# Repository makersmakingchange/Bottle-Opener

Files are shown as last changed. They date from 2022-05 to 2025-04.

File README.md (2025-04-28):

# Bottle Opener
The Bottle Opener is a simple, low-cost, 3D-printable handheld tool to help those with arthritis, limited finger dexterity or other related disabilities open or close plastic screw-on caps on various beverage bottles, cleaning products, condiments. The bottle opener allows users to remove or replace the lids of these jugs with a small squeeze on a large, rounded gripping surface. The Bottle Opener has several modified versions to open different sizes of containers. The different sizes are named by the approximate diameter of the caps they can open in millimeters.

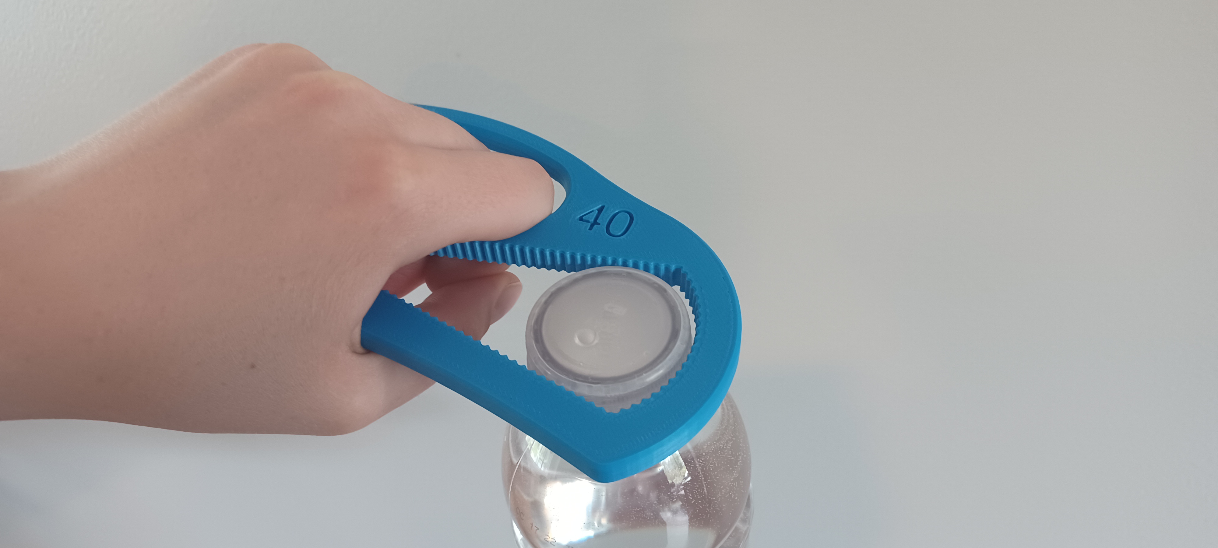
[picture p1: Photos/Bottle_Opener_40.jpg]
Bottle_Opener


## More info at
- [Makers Making Change Project Page](https://makersmakingchange.com/project/bottle-opener/)

## Getting Started

### 1. Print the 3D Printable components

Print the components according to the instructions in the [3D Print Guide](/Documentation/Bottle_Opener_3D_Print_Guide_V1.0.pdf).

All of the files and individual print files can be in the [/Build_Files](/Build_Files) folder.

### 2. Sizing

There are 5 different sizes of bottle opener to suit the different sizes of plastic caps on various bottles and containers. The [Summary](/Documentation/Bottle_Opener_Summary_V1.0.pdf) contains information on examples of different bottles that can be opened with the different sizes of bottle openers. A [Printable Sizing Sheet](/Documentation/Bottle_Opener_Printable_Sizing_Chart.pdf) has been provided to match bottle caps to the suitable bottle opener. Make sure to check "actual size" in the print settings so the image remains to-scale.

### 3. Bill of Materials

The [Bill of Materials](/Documentation/Bottle_Opener_BOM_V1.0.csv) lists the cost of building the different sizes of Bottle Openers.

## Files
### Documentation
| Document              | Version | Link |
|-----------------------|---------|------|
| Summary               | 1.0     | [Bottle_Opener_Summary](/Documentation/Bottle_Opener_Summary_V1.0.pdf)     |
| 3D Print Guide        | 1.0     | [Bottle_Opener_3D_Print_Guide](/Documentation/Bottle_Opener_3D_Print_Guide_V1.0.pdf)     |
| Design Rationale      | 1.0     | [Bottle_Opener_Design_Rationale](/Documentation/Bottle_Opener_Design_Rationale_V1.0.pdf)     |
| Bill of Materials     | 1.0     | [Bottle_Opener_Bill_of_Materials](/Documentation/Bottle_Opener_BOM_V1.0.csv)     |
| Maker Checklist       | 1.0     | [Bottle_Opener_Maker_Checklist](/Documentation/Bottle_Opener_Maker_Checklist_V1.0.pdf)     |
| User Guide            | 1.0     | [Bottle_Opener_User_Guide](/Documentation/Bottle_Opener_User_Guide_V1.0.pdf)    |
| Changelog             | 1.0     | [Bottle_Opener_Changelog](/Documentation/Bottle_Opener_Changelog_V1.0.pdf)     |
| Printable Sizing Chart| 1.0     | [Bottle_Opener_Printable_Sizing_Chart](/Documentation/Bottle_Opener_Printable_Sizing_Chart.pdf)     |

### Design Files
 - [CAD Files](/Design_Files/CAD_Files/)
   - [STEP Files](/Design_Files/CAD_Files/Step_Files/)
   - [Autodesk Fusion Files](/Design_Files/CAD_Files/Autodesk_Fusion/)
   - [Profile Sketch](/Design_Files/CAD_Files/Bottle_Opener_40_Sketch.png)

### Build Files
 - [3D Printing Files](/Build_Files)

## Attribution
The source of the original design is unknown. Various improvement and documentation have been completed by the Neil Squire Society / Makers Making Change.

### Contributors
 - Amanda Tuey. Neil Squire / Makers Making Change.
 - Kristina Mok. Neil Squire / Makers Making Change.
 - Taz Oldaker. Neil Squire / Makers Making Change.
 - Jake McIvor. Neil Squire / Makers Making Change.

## License
<br /><span xmlns:dct="http://purl.org/dc/terms/" property="dct:title">Bottle Opener</span> by <a xmlns:cc="http://creativecommons.org/ns#" href="www.makersmakingchange.com" property="cc:attributionName" rel="cc:attributionURL">Neil Squire</a> is licensed under a <a rel="license" href="http://creativecommons.org/licenses/by-sa/4.0/">Creative Commons Attribution-ShareAlike 4.0 International License</a>.

---
<!-- ABOUT MMC START -->
## About Makers Making Change
[Makers Making Change Logo](https://www.makersmakingchange.com/)

Makers Making Change is a program of [Neil Squire](https://www.neilsquire.ca/), a Canadian non-profit that uses technology, knowledge, and passion to empower people with disabilities.

Makers Making Change leverages the capacity of community based Makers, Disability Professionals and Volunteers to develop and deliver affordable Open Source Assistive Technologies.

 - Website: [www.MakersMakingChange.com](https://www.makersmakingchange.com/)
 - GitHub: [makersmakingchange](https://github.com/makersmakingchange)
 - Bluesky: [@makersmakingchange.bsky.social](https://bsky.app/profile/makersmakingchange.bsky.social)
 - Instagram: [@makersmakingchange](https://www.instagram.com/makersmakingchange)
 - Facebook: [makersmakechange](https://www.facebook.com/makersmakechange)
 - LinkedIn: [Neil Squire Society](https://www.linkedin.com/company/neil-squire-society/)
 - Thingiverse: [makersmakingchange](https://www.thingiverse.com/makersmakingchange/about)
 - Printables: [MakersMakingChange](https://www.printables.com/@MakersMakingChange)

### Contact Us
For technical questions, to get involved, or to share your experience we encourage you to [visit our website](https://www.makersmakingchange.com/) or [contact us](https://www.makersmakingchange.com/s/contact).
<!-- ABOUT MMC END -->

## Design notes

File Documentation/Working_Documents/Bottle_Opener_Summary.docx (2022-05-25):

# Title

Bottle Opener

## Subtitle

A tool to open screw on caps up to 50 mm in diameter.

## Device Specifications

Stage: Recently Added

Designer: Makers Making Change

Material Cost: $0 - $10

Disability Type: Mobility / Physical

Capabilities Needed: 3D Printing

Usage:

- Aids for Daily Living (ADL)
- Mobility

Difficulty: Beginner

Time to Complete: 1-4hr

License: Attribution - Non-Commercial - ShareAlike 4.0 International

## Device Details

### Overview

The Bottle Opener is a simple, low-cost, 3D-printable handheld tool to help those with arthritis, limited finger dexterity or other related disabilities open or close plastic screw-on caps on various beverage bottles, cleaning products, condiments. The bottle opener allows users to remove or replace the lids of these jugs with a small squeeze on a large, rounded gripping surface. The Bottle Opener has several modified versions to open different sizes of containers. The different sizes are named by the approximate diameter of the caps they can open in millimeters.

### Usage

Slide the toothed gripping surface on top of the lid of the container, then while squeezing the handle to grip the lid, twist either the container or the device to remove or screw on the lid.

### Cost

The cost of this device includes only the filament used to 3D print the device/devices. Each device requires slightly over $1 CAD worth of PLA filament.

### Build Instructions

This device consists of a single 3d printed part. The necessary files and 3D printing instructions are provided in the linked GitHub repository.

#### Skills Required

- 3D Printing

#### Time Required

- 3D Printing: ~3.5 hours

#### 3D Printing

Refer to the Large Bottle Opener 3D Printing Guide.

Sizing

There are five different sizes of Bottle Openers to suit different size caps on bottles and containers.

Bottle Opener Version | Compatible Diameter of Caps | Examples of compatible Bottles and Containers (May vary between brands) | Image Example of compatible Bottles

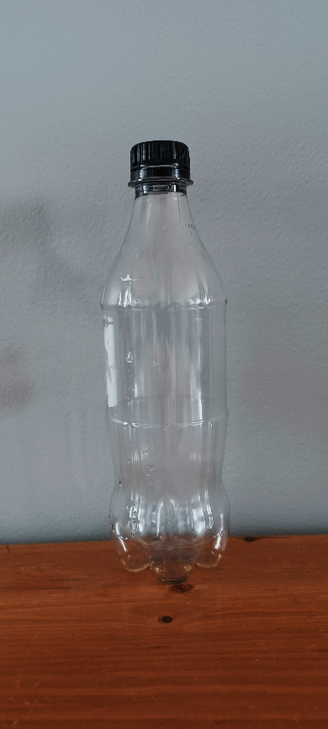
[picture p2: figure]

Bottle Opener 30 | 28 – 30 mm | - Pop bottles of all sizes (355 mL to 2 L) - Bottled Water of all sizes (355 mL to 2 L) - Milk Carton 2 L - Juice Carton 2 L

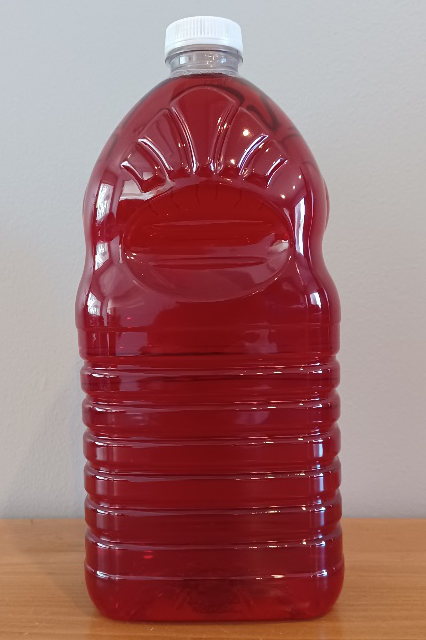
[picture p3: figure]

Bottle Opener 35 | 33 – 36 mm | - Juice Jug (Some brands) 1.89 L - Ketchup Bottle 1 L - Juice Carton 900 mL

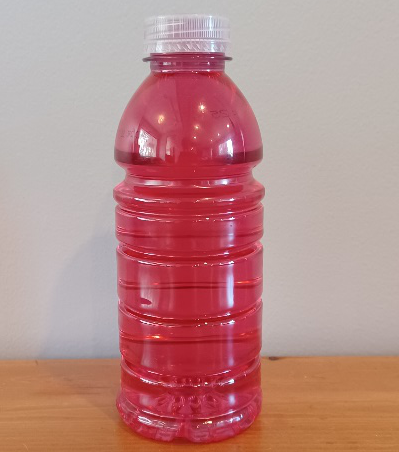
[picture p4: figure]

Bottle Opener 40 | 38 – 41 mm | - Sports Drink 591 mL - Sports Drink 950 mL - Juice Bottle 473 mL - Iced Tea Bottle 473 mL - Milk Bottle 473 mL - Milk Jug 2 L - Milk Jug 4 L - Kefir Bottle 1 L

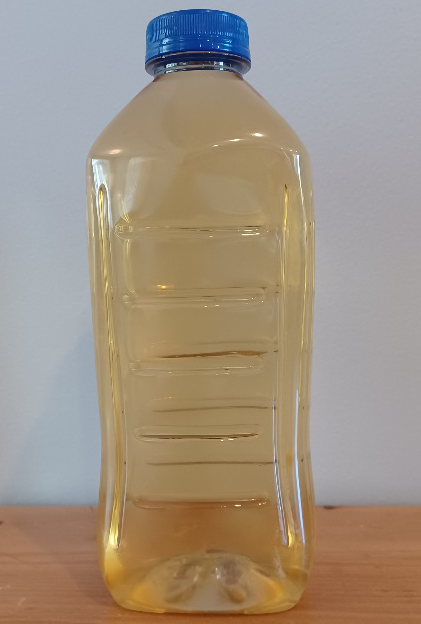
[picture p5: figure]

Bottle Opener 45 | 43 – 46 mm | - Juice Jug 1.46 L - Juice Jug (Some Brands) 1.89 L - Juice Jug 945 mL

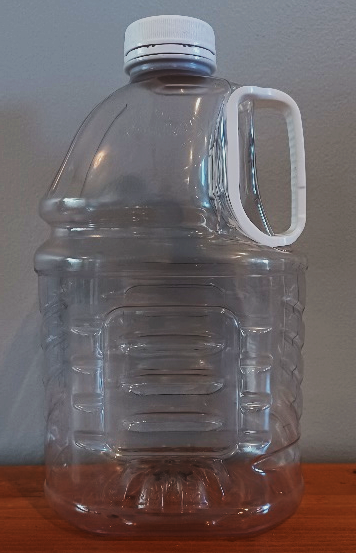
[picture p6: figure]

Bottle Opener 50 | 48 – 51 mm | - 3 L Juice Jug

## Sizing Helper Chart:

A printable to-scale document is included to match a specific cap size to the appropriate bottle opener. To successfully print, check “actual size” in the print settings. Once the document is printed, a scale check line has been included to test if the document correctly printed to scale.

### Attribution

The original and modified version of this design, as well as the documentation, was created by Neil Squire / Makers Making Change.

© 2022 by Neil Squire / Makers Making Change. This work is licensed under the CC BY SA 4.0 License: http://creativecommons.org/licenses/by-sa/4.0 Files available at https://makersmakingchange.com/project/bottle-opener/ Page 1 of 2

V1.0 | May 2022 Bottle Opener Summary

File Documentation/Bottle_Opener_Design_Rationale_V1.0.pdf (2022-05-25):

V1.0 | May 2022

## Bottle Opener

## DESIGN RATIONALE

© 2022 by Neil Squire / Makers Making Change. This work is licensed under the CC BY SA 4.0 License: http://creativecommons.org/licenses/by-sa/4.0 Files available at https://makersmakingchange.com/project/bottle-opener/

### Introduction

The Bottle Opener provides a way for those with arthritis, limited finger dexterity or other related disabilities to open the lids on disposable beverage bottles. The original bottle opener, now named Bottle Opener 30, was created in February 2018. This design can open most pop bottles and disposable water bottles but cannot open the larger lids commonly seen on sports drinks, juice jugs and other bottles and containers. More sizes have been created to open various sizes of larger lids.

There are several somewhat “standard” sizes for the lids of beverage bottles. Some beverage bottles currently available in grocery stores in Victoria, B.C. are listed below:

All measurements of cap diameters are within 2mm less and 1mm greater than the listed value.
30mm | 35mm | 40mm | 45mm | 50mm
2 L pop bottle | 1.89 L western family juice jug | 591 mL Vitamin Water bottle | 1.46 L SunRype Juice Jug | 3 L Ocean Spray juice jug
1 L pop bottle | 1 L Ketchup Bottle | 950 mL Gatorade bottle | 1.89 L Ocean Spray Juice Jug
710 mL pop bottle | 400 mL HP Sauce | 4 L Milk Jug | 945 mL Welch’s Prune Nectar
591 mL pop bottle | 900 mL SunRype Juice Carton. | 2 L Milk Jug | 1.89 L Mott’s Clamato Jug
355 mL pop bottle | | 473 mL Milk 2 go bottle
500 mL water bottle | | 1 L Liberte Kefir

2 L Milk Carton

### Goals

G01 | The device should cost less than the commercially available option.
G02 | The device should provide an easier way to open large juice jugs for those with arthritis or limited finger dexterity.

### Functional Requirements

F01 | The device must adequately grip it’s specific juice jug’s lid to remove the factory seal.
F02 | The device must easily slide on top on the juice jug lid such that there is some clearance between the lid and the device.

## DESIGN RATIONALE

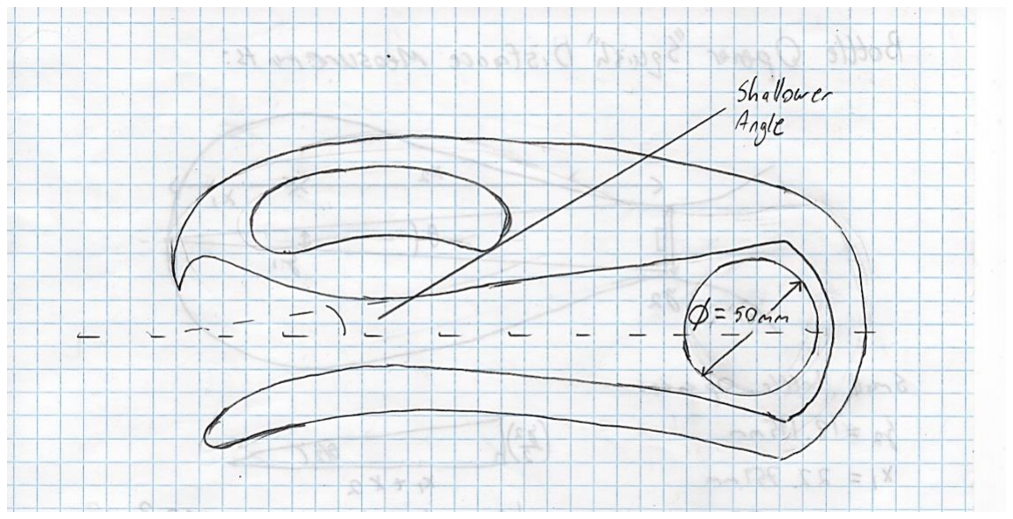
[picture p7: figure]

© 2022 by Neil Squire / Makers Making Change.

### Non-functional Requirement

NF01 | The device must not engage any discomfort in the user’s hand.
NF02 | The device must be manufacturable in a single 3D print using PLA without the use of support material.
NF03 | The device must not deform under the stress of daily use.

### Constraints

C01 Single-build cost must be less than $13

### Ideation

The new sizes of Bottle Openers aims to maintain the functionality of the original bottle opener while allowing for larger bottles. Some of the design considerations to accomplish this task include:
| • Keeping the same handle dimensions and the same motion to squeeze the cap. • Keeping the same general size for the device. • Ensuring the Large Bottle Opener is not more difficult squeeze to grip the cap. • Ensuring the Large Bottle Opener has adequate gripping capacity to open the lid.

### Conceptual Design

The original handle and general shape will be copied with the cap opening being extended.

### Concept 1

Extend the original angled toothed faces so that the gripping surface is identical, but the

## DESIGN RATIONALE

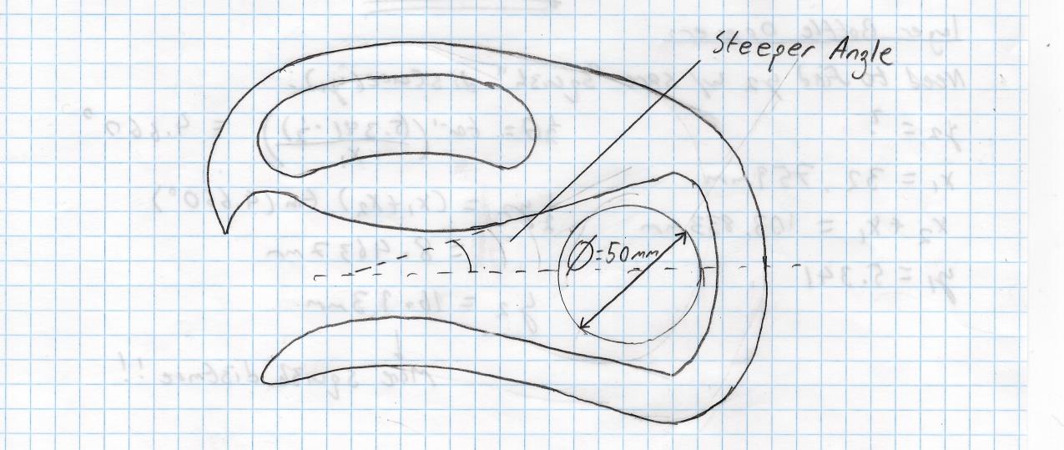
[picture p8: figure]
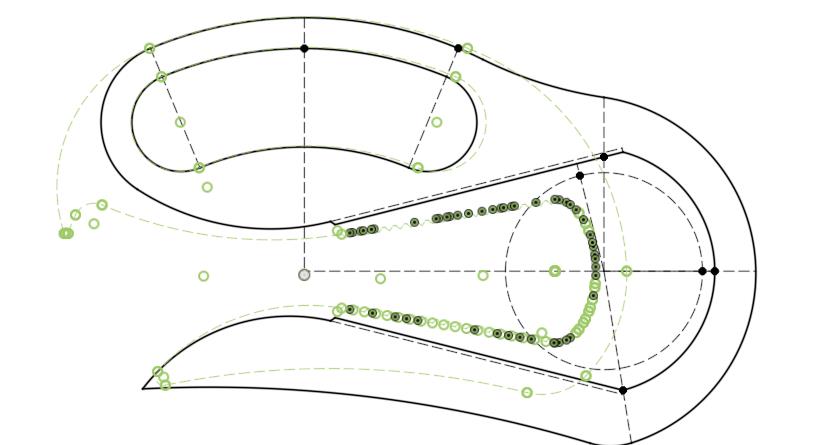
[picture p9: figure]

© 2022 by Neil Squire / Makers Making Change.

### Concept 2

Steepen the angles and adjust the geometery to create a device of similar length. This design would create a smaller device, allowing for less material to be used making manufacturing quicker and more environmentally sustainable.

### Detailed Design

Both conceptual designs were considered so that the gripping surface, gripping angle, length of device and material usage were optimized.

The general outlines of both the large bottle opener (Black) and the original bottle opener (Green) are shown below.

## DESIGN RATIONALE

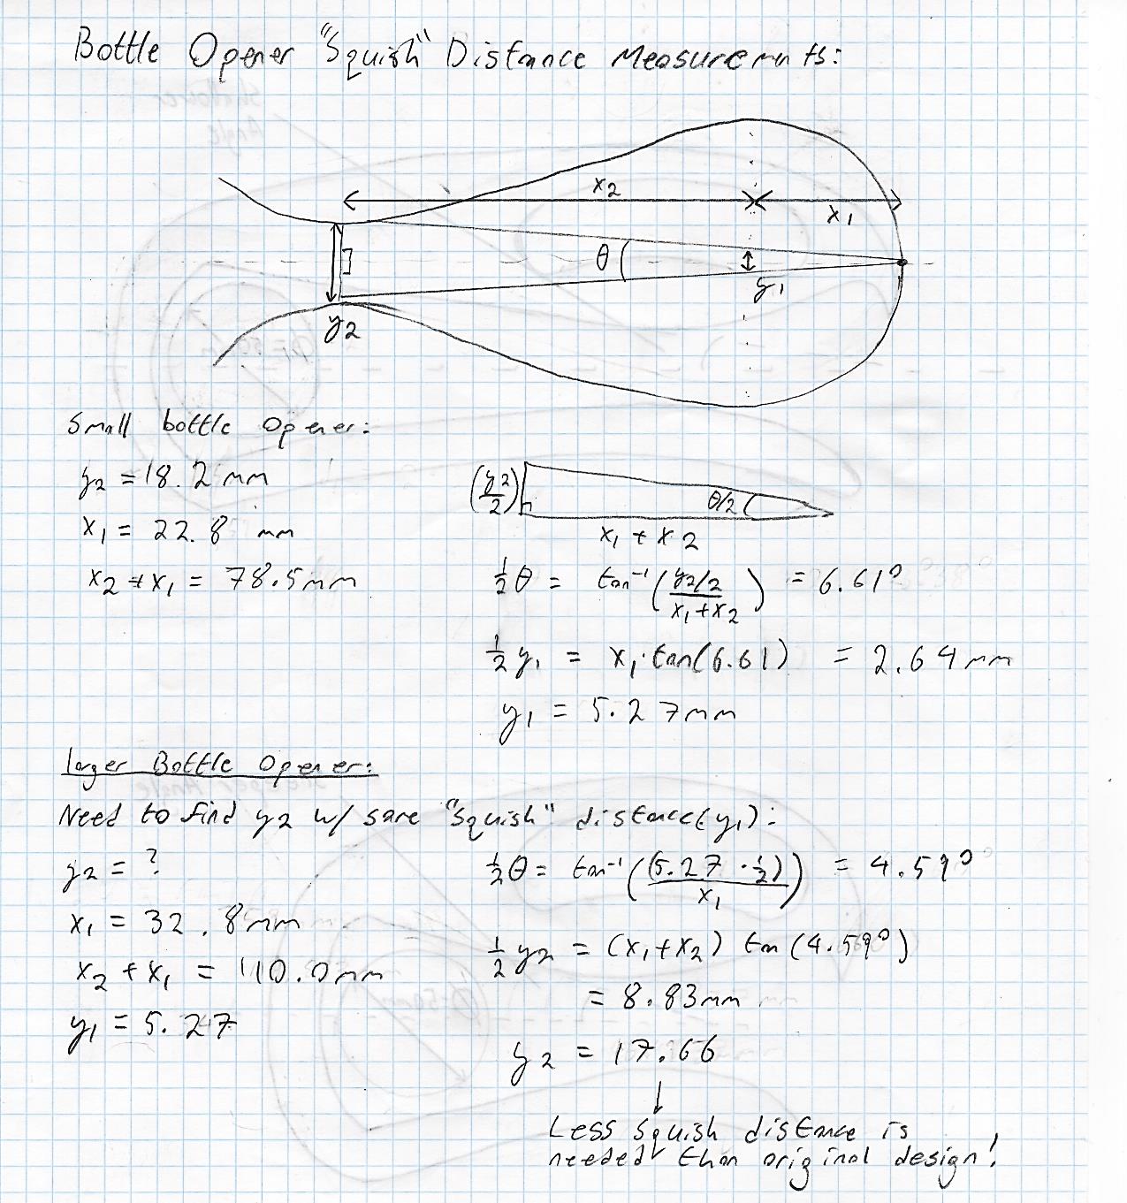
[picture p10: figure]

© 2022 by Neil Squire / Makers Making Change.

The following calculation was done to ensure that the new design had enough “squeezing” distance to grip the cap. With the cap further away from the handle, squeezing the handle would result in less of that squeeze translating to movement in the cap end.

The result was that more distance between handles to squeeze the cap was not necessary. However, in testing it was found, possibly due to the longer flexing surface, that the device still needed a slightly bigger gap in this area to provide satisfactory grip, so this distance was increased anyway.

## DESIGN RATIONALE

© 2022 by Neil Squire / Makers Making Change.

### Opportunities for Improvement

- A design could be considered that allows for the opening of multiple bottle cap sizes in one device.
- More designs could be made to suit different sizes of bottles.

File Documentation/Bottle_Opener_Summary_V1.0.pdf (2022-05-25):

V1.0 | May 2022

## Bottle Opener

## SUMMARY

© 2022 by Neil Squire / Makers Making Change. This work is licensed under the CC BY SA 4.0 License: http://creativecommons.org/licenses/by-sa/4.0 Files available at https://makersmakingchange.com/project/bottle-opener/

### Title

Bottle Opener

### Subtitle

A tool to open screw on caps up to 50 mm in diameter.

### Device Specifications

Stage: Recently Added

Designer: Makers Making Change

Material Cost: $0 - $10

Disability Type: Mobility / Physical

Capabilities Needed: 3D Printing

Usage:
- Aids for Daily Living (ADL)
- Mobility

Difficulty: Beginner

Time to Complete: 1-4hr

License: Attribution - Non-Commercial - ShareAlike 4.0 International

### Device Details

Overview
The Bottle Opener is a simple, low-cost, 3D-printable handheld tool to help those with arthritis, limited finger dexterity or other related disabilities open or close plastic screw-on caps on various beverage bottles, cleaning products, condiments. The bottle opener allows users to remove or replace the lids of these jugs with a small squeeze on a large, rounded gripping surface. The Bottle Opener has several modified versions to open different sizes of containers. The different sizes are named by the approximate diameter of the caps they can open in millimeters.

Usage
Slide the toothed gripping surface on top of the lid of the container, then while squeezing the handle to grip the lid, twist either the container or the device to remove or screw on the lid.

## SUMMARY

© 2022 by Neil Squire / Makers Making Change.

Cost
The cost of this device includes only the filament used to 3D print the device/devices. Each device requires slightly over $1 CAD worth of PLA filament.

Build Instructions
This device consists of a single 3d printed part. The necessary files and 3D printing instructions are provided in the linked GitHub repository.

Skills Required
- 3D Printing

Time Required
- 3D Printing: ~3.5 hours

3D Printing
Refer to the Large Bottle Opener 3D Printing Guide.

Sizing
There are five different sizes of Bottle Openers to suit different size caps on bottles and containers.

Bottle Opener
Version

Compatible
Diameter of
Caps

Examples of compatible
Bottles and Containers (May vary between brands)

Image Example of compatible Bottles

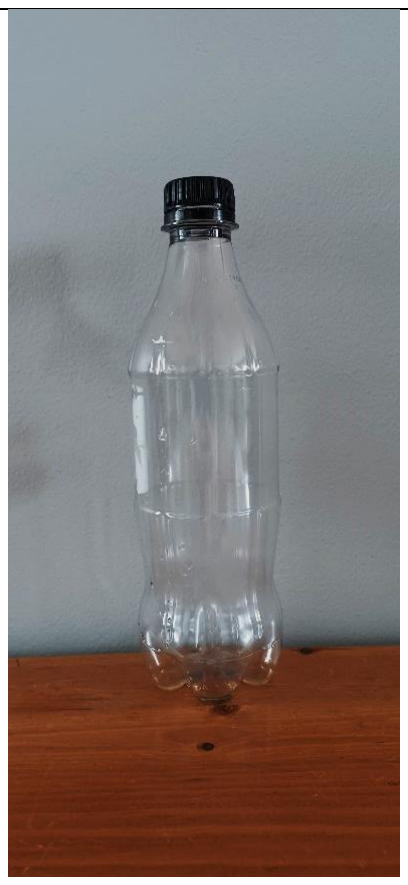
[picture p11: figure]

Bottle Opener 30 28 – 30 mm

- Pop bottles of all sizes (355 mL to 2 L)
- Bottled Water of all
sizes (355 mL to 2 L)
- Milk Carton 2 L
- Juice Carton 2 L

## SUMMARY

© 2022 by Neil Squire / Makers Making Change.

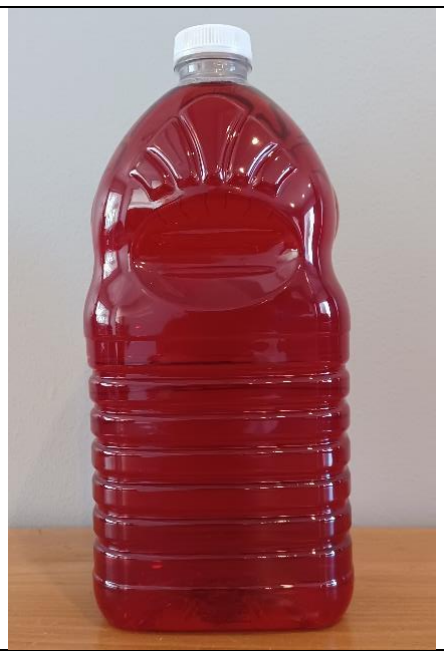
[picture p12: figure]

Bottle Opener 35 | 33 – 36 mm | • Juice Jug (Some brands) 1.89 L • Ketchup Bottle 1 L • Juice Carton 900 mL

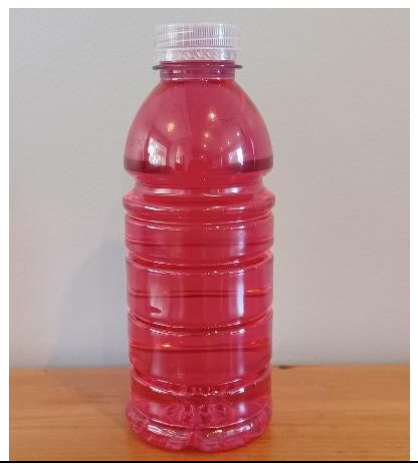
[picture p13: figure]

Bottle Opener 40 | 38 – 41 mm | • Sports Drink 591 mL • Sports Drink 950 mL • Juice Bottle 473 mL • Iced Tea Bottle 473 mL • Milk Bottle 473 mL • Milk Jug 2 L • Milk Jug 4 L • Kefir Bottle 1 L

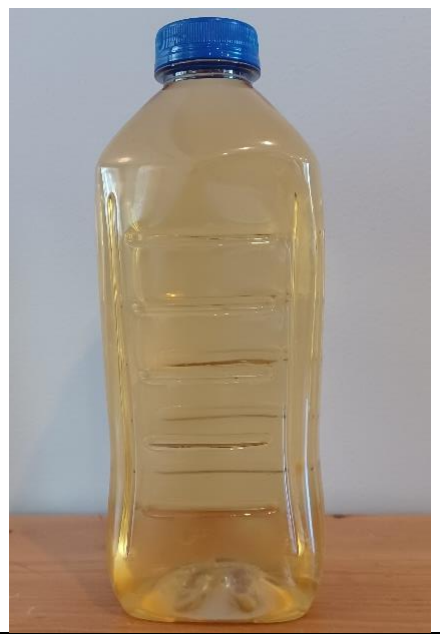
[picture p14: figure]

Bottle Opener 45 | 43 – 46 mm | • Juice Jug 1.46 L • Juice Jug (Some Brands) 1.89 L • Juice Jug 945 mL
Bottle Opener 50 | 48 – 51 mm | • 3 L Juice Jug

## SUMMARY

© 2022 by Neil Squire / Makers Making Change.

Sizing Helper Chart:

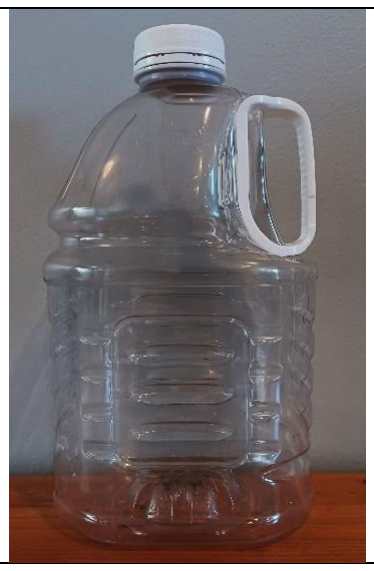
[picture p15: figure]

A printable to-scale document is included to match a specific cap size to the appropriate bottle opener. To successfully print, check “actual size” in the print settings. Once the document is printed, a scale check line has been included to test if the document correctly printed to scale.

Attribution
The original and modified version of this design, as well as the documentation, was created by Neil Squire / Makers Making Change.

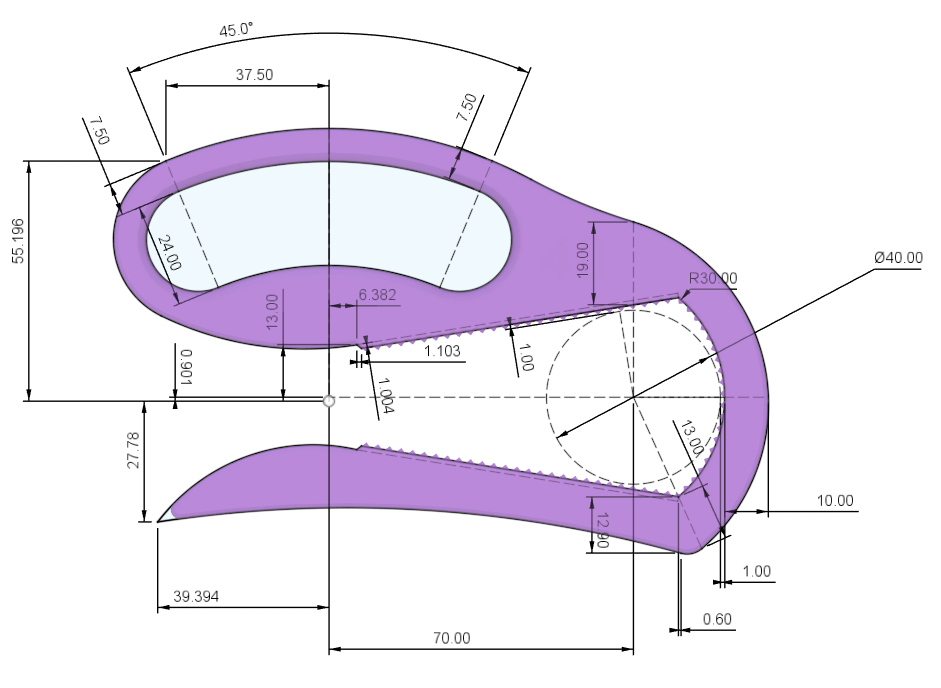
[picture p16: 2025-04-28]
Design_Files/CAD_Files/Bottle_Opener_40_Sketch.png

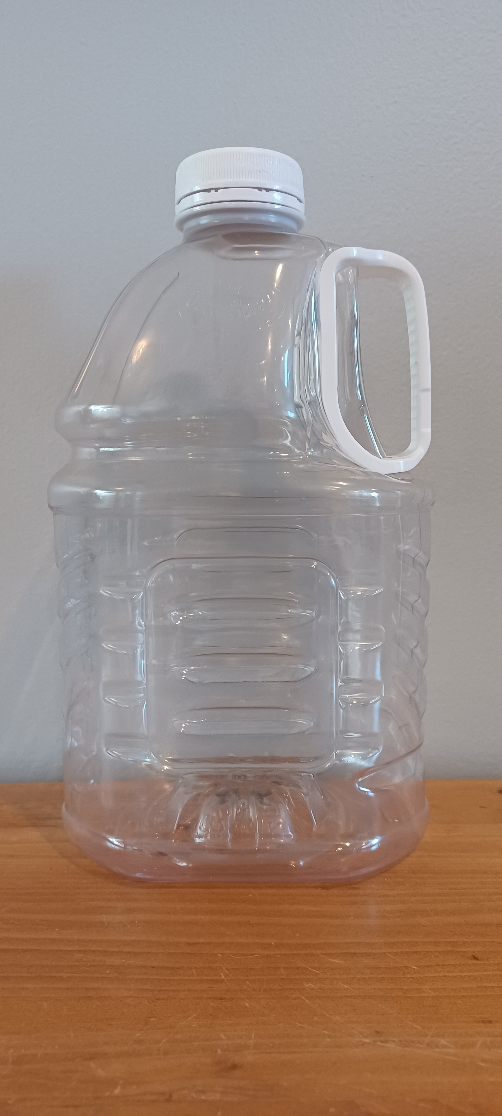
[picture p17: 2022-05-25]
Photos/Example_Bottle_50.jpg

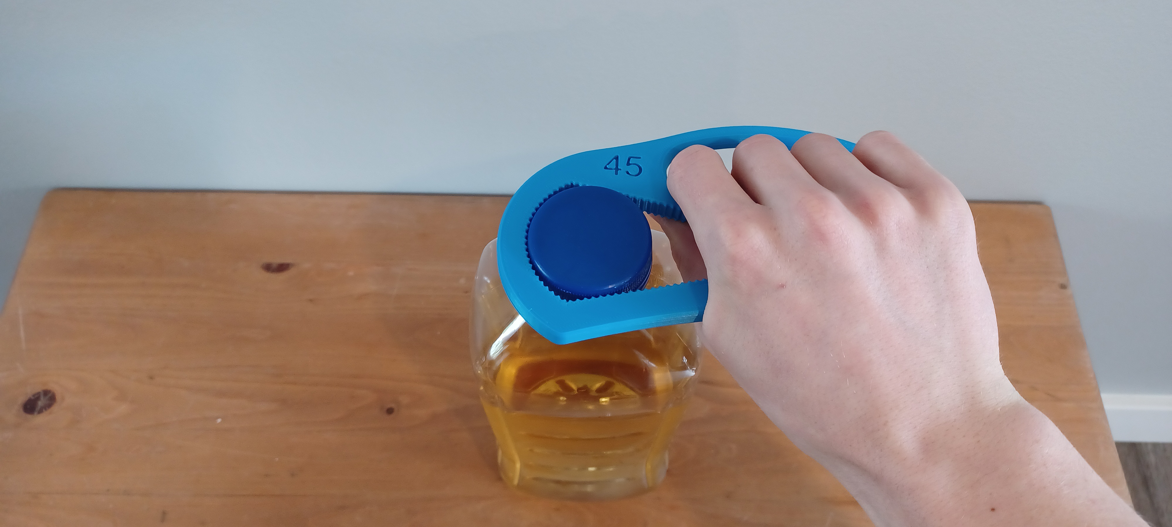
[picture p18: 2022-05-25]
Photos/Bottle_Opener_45.jpg

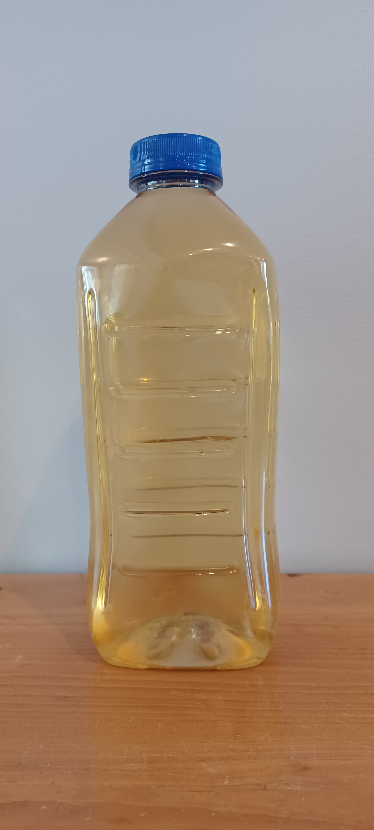
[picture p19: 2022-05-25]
Photos/Example_Bottle_45.jpg

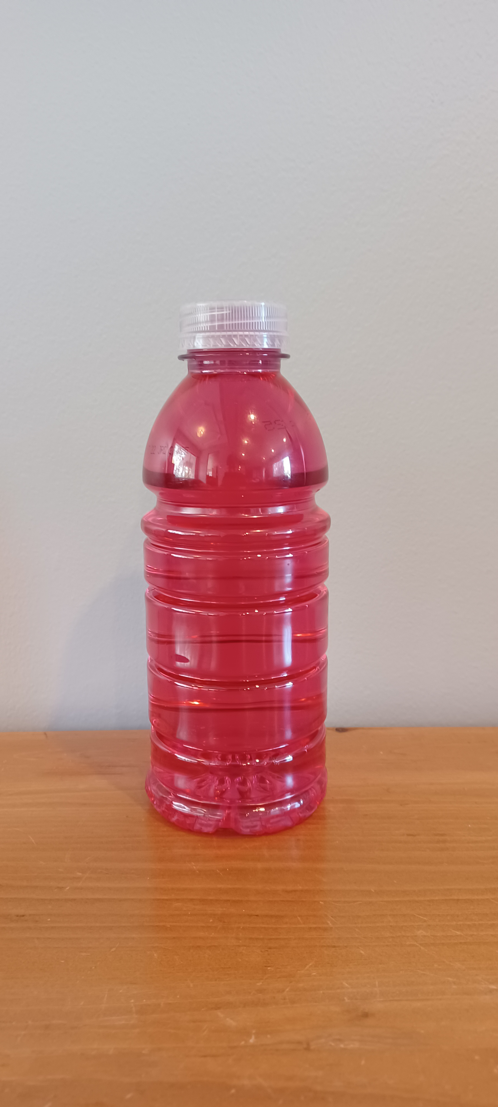
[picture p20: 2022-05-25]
Photos/Example_Bottle_40.jpg

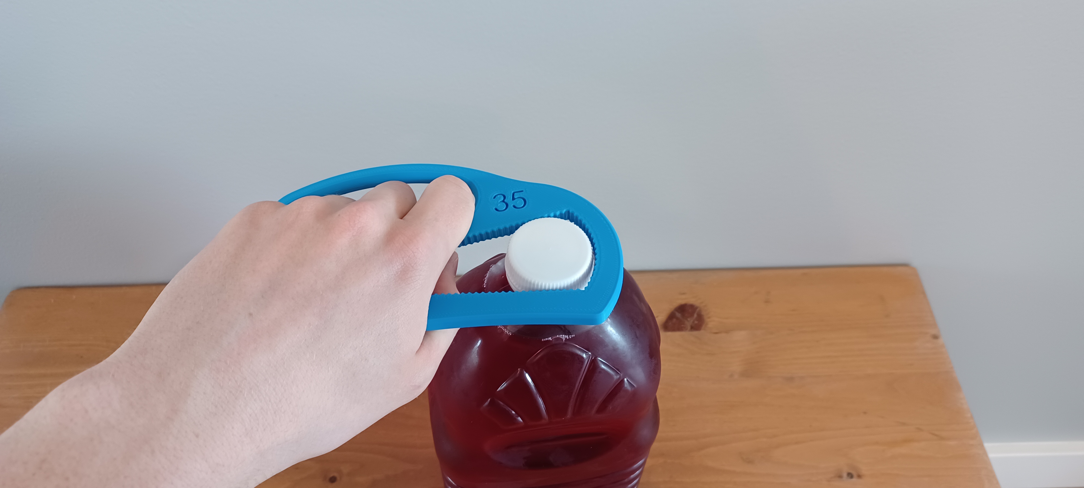
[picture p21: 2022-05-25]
Photos/Bottle_Opener_35.jpg

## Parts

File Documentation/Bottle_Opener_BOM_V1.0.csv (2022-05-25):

Device: Bottle_Opener |  | Total Cost | Total Print time (hr) | Total filament (g)
Version: V1.0 | Date Created: 5/18/2022 | $4.65 | 3.78 | 37
3D Printed Parts ESTIMATED PRICING USING 1KG ROLL COST: | $25.00
Part | Description | Quantity Needed | TOTAL Mass (g) | Estimated Price | Print Time (Min) | Link
Bottle_Opener_30.stl | STL file for full functional bottle opener with nominal diameter of approx. 30 mm. | 1 | 37 | $0.93 | 227 | Bottle-Opener/Build_Files at main · makersmakingchange/Bottle-Opener (github.com)
Bottle_Opener_35.stl | STL file for full functional bottle opener with nominal diameter of approx. 30 mm. | 1 | 36 | $0.90 | 224
Bottle_Opener_40.stl | STL file for full functional bottle opener with nominal diameter of approx. 30 mm. | 1 | 36 | $0.90 | 226
Bottle_Opener_45.stl | STL file for full functional bottle opener with nominal diameter of approx. 30 mm. | 1 | 38 | $0.95 | 231
Bottle_Opener_50.stl | STL file for full functional bottle opener with nominal diameter of approx. 30 mm. | 1 | 39 | $0.98 | 241
 |  |  | Total Print Cost: | $4.65

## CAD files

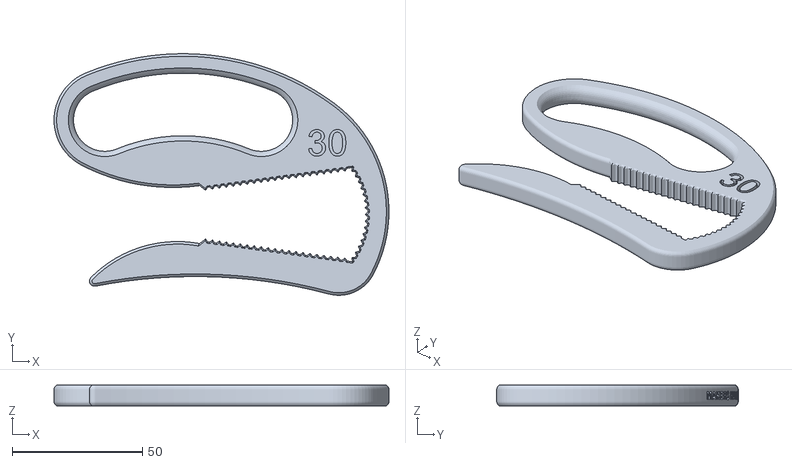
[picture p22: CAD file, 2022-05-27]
Build_Files/Bottle_Opener_30.stl
128.6 x 92.7 x 8.00

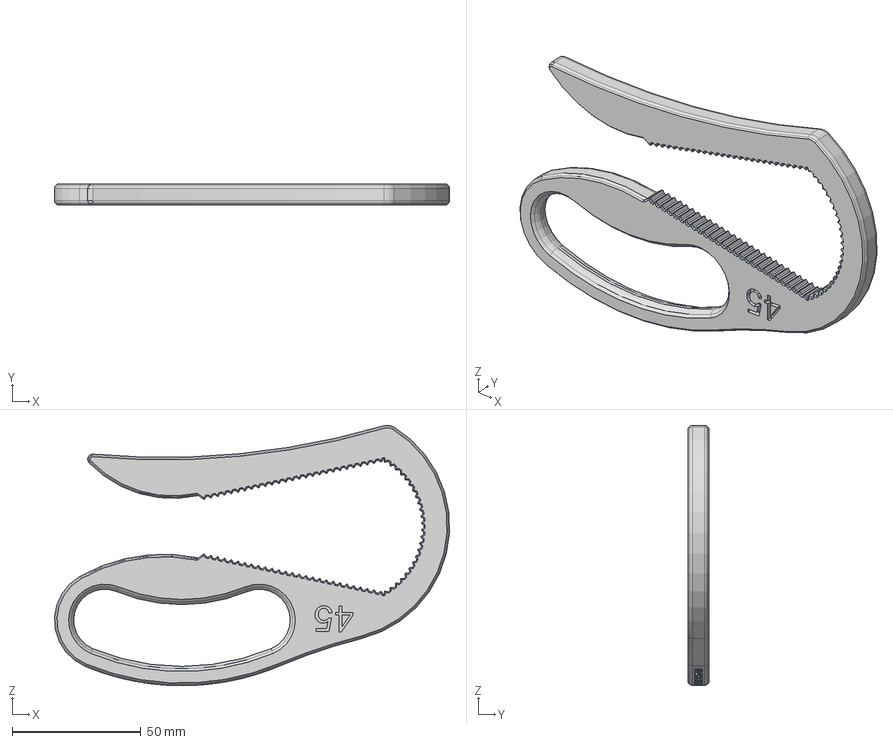
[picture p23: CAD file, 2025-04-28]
Design_Files/CAD_Files/Step_Files/Bottle_Opener_45.step
153.4 x 8.00 x 101.2 mm

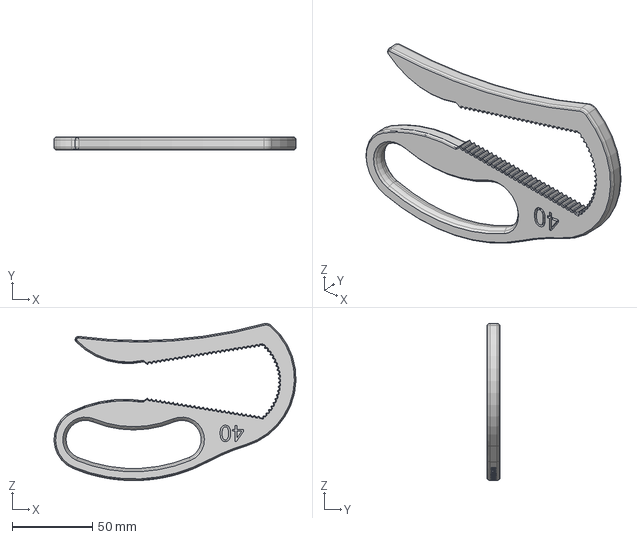
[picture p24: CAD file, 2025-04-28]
Design_Files/CAD_Files/Step_Files/Bottle_Opener_40.step
150.5 x 8.00 x 97.8 mm

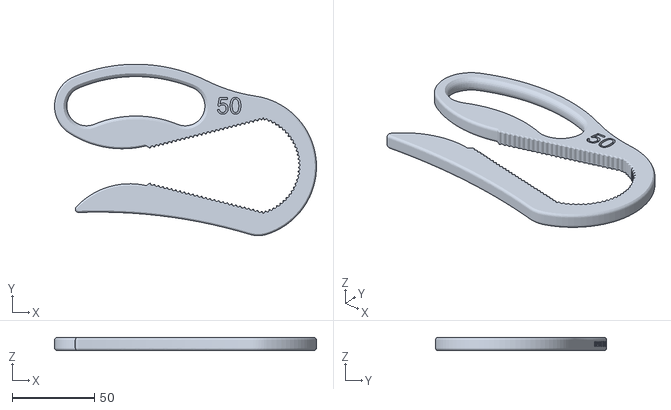
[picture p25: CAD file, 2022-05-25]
Build_Files/Bottle_Opener_50.stl
159.5 x 104.4 x 8.00

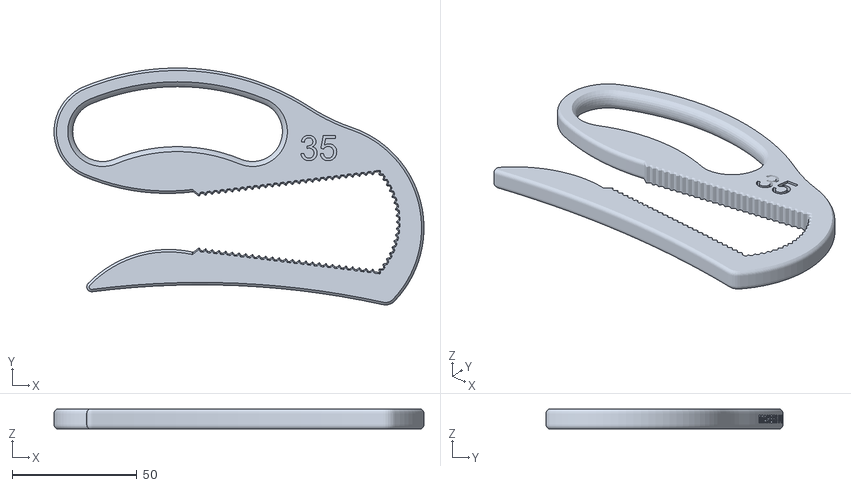
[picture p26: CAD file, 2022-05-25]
Build_Files/Bottle_Opener_35.stl
148.3 x 95.0 x 8.00

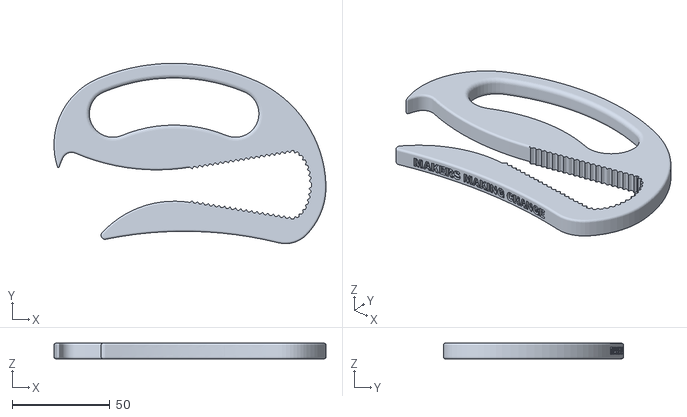
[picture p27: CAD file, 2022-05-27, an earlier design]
Bottle_Opener_Archive/Archived Build Files/Bottle_Opener_v.1.0.0.STL
138.8 x 92.0 x 8.00

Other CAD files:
Build_Files/Bottle_Opener_45.stl
Design_Files/CAD_Files/Step_Files/Bottle_Opener_50.step
Build_Files/Bottle_Opener_40.stl
Design_Files/CAD_Files/Step_Files/Bottle_Opener_30.step
Design_Files/CAD_Files/Step_Files/Bottle_Opener_35.step
Bottle_Opener_Archive/Archived Design Files/Bottle_Opener_v.1.0.0 v1.f3d
Design_Files/CAD_Files/Autodesk_Fusion/Bottle_Opener_30.f3d
Design_Files/CAD_Files/Autodesk_Fusion/Bottle_Opener_35.f3d
Design_Files/CAD_Files/Autodesk_Fusion/Bottle_Opener_40.f3d
Design_Files/CAD_Files/Autodesk_Fusion/Bottle_Opener_45.f3d
Design_Files/CAD_Files/Autodesk_Fusion/Bottle_Opener_50.f3d

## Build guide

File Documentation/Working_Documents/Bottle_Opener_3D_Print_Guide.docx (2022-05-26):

# 3D Printing Summary

Metrics
Total Print Time (min) | 224 - 241
Total Number of Components | 1 - 5
Typical Total Mass (g) | 36 - 39
Typical Number of Print Setups | 1 - 5

# 3D Printing Settings

Print File Name | Qty | Total Print Time (hr:min) | Mass (g) | Infill (%) | Support | Layer Height/ Nozzle Diameter(mm) | Notes (orientation, special settings, etc.)
Bottle_Opener_30.stl | 1 | 3:47 | 37 | 50 | No Support | 0.2/0.4 | Adjust number of perimeters to 3-4.
Bottle_Opener_35.stl | 1 | 3:44 | 36 | 50 | No Support | 0.2/0.4 | Adjust number of perimeters to 3-4.
Bottle_Opener_40.stl | 1 | 3:46 | 36 | 50 | No Support | 0.2/0.4 | Adjust number of perimeters to 3-4.
Bottle_Opener_45.stl | 1 | 3:51 | 38 | 50 | No Support | 0.2/0.4 | Adjust number of perimeters to 3-4.
Bottle_Opener_50.stl | 1 | 4:01 | 39 | 50 | No Support | 0.2/0.4 | Adjust number of perimeters to 3-4.

# Post-Processing

- Remove any burrs or sharp edges that may occur if applicable.

# Customization Options

- There are parameters given in the CAD file (.f3d) to change the cap size and handle size if desired.
- Can be printed in any colour.

# Examples of Quality Prints:

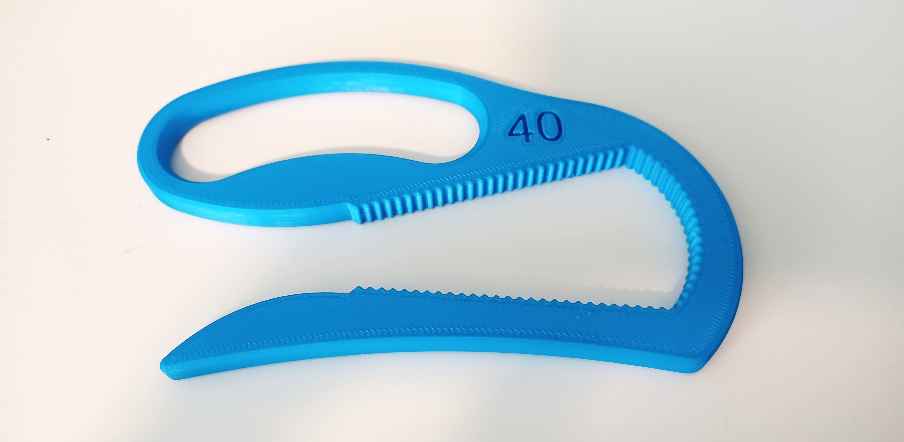
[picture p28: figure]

Example of Bottle Opener 40

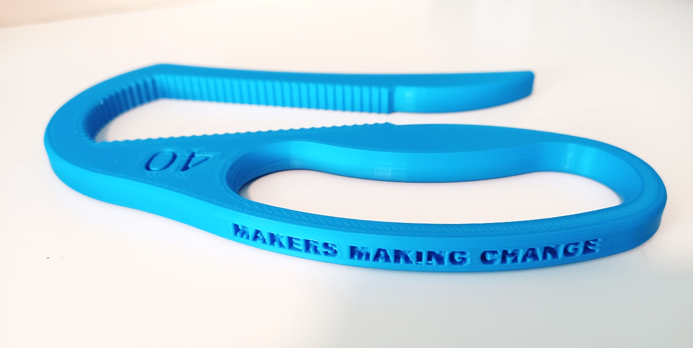
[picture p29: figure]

Example of Bottle Opener 40

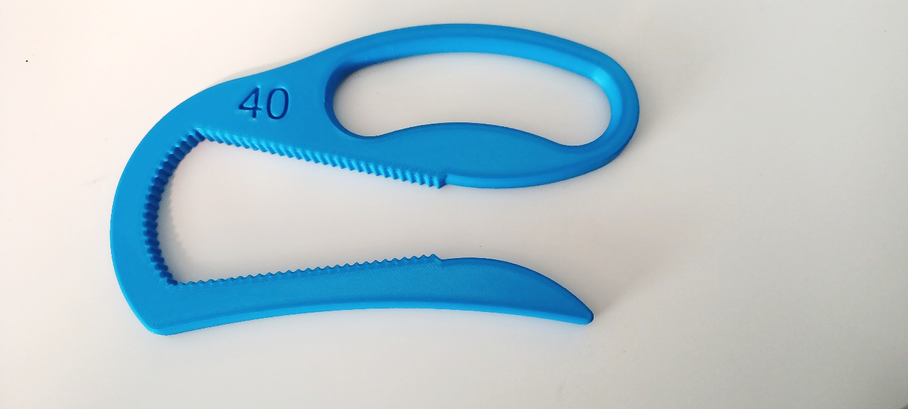
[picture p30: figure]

Example of Bottle Opener 40

© 2022 by Neil Squire / Makers Making Change. This work is licensed under the CC BY SA 4.0 License: http://creativecommons.org/licenses/by-sa/4.0 Files available at https://makersmakingchange.com/project/bottle-opener/ Page 1 of 2

V1.0| May 2022 Bottle Opener 3D Printing Guide

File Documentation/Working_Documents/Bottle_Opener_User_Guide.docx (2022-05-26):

## Introduction

The Large Bottle Opener is a tool to help those with arthritis, limited finger dexterity or other related disabilities open the screw-on caps commonly seen on large juice jugs.

## Usage

Grip the bottle opener with fingers placed though the hole and palm on the bottom lever. Place the bottle opener over the lid of the bottle, squeeze the lever while twisting the cap off the bottle.

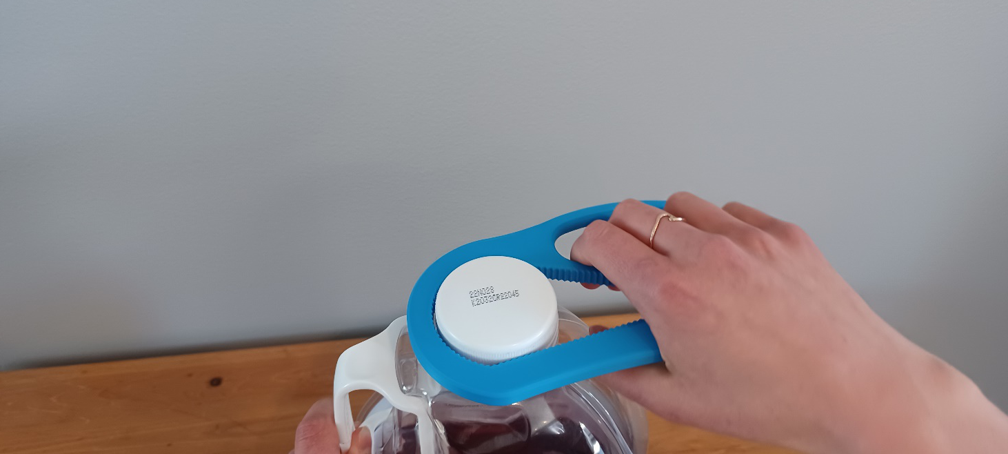
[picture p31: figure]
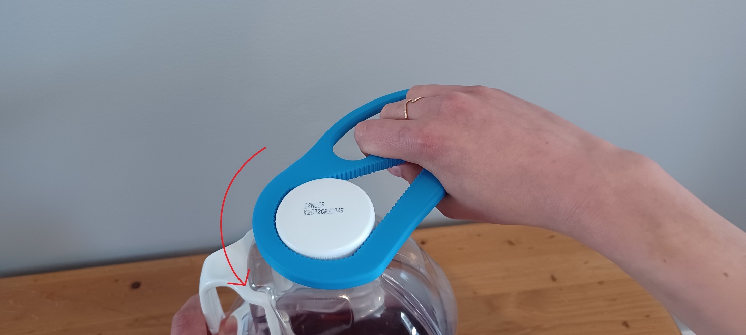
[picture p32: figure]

## Compatibility

Bottle Opener Version | Compatible Diameter of Caps | Examples of compatible Bottles and Containers (May vary between brands) | Image Example of compatible Bottles

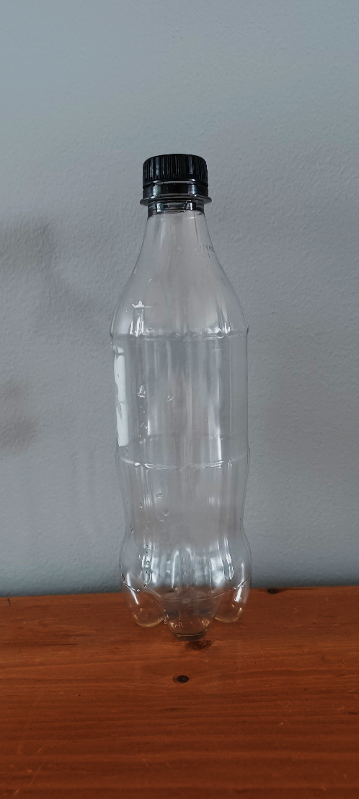
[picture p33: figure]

Bottle Opener 30 | 28 – 30 mm | - Pop bottles of all sizes (355 mL to 2 L) - Bottled Water of all sizes (355 mL to 2 L) - Milk Carton 2 L - Juice Carton 2 L

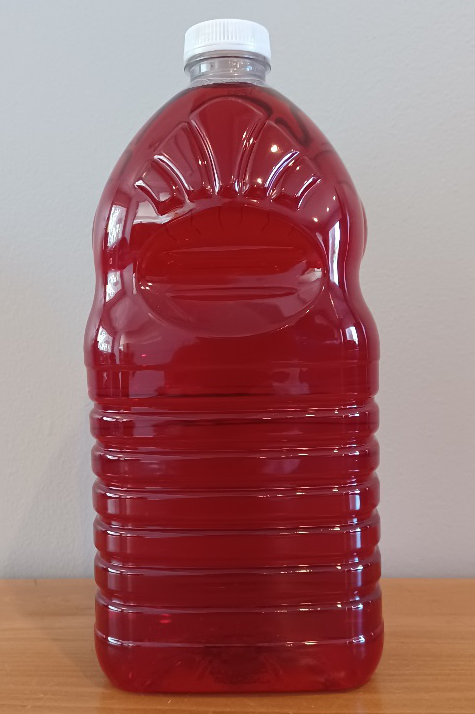
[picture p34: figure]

Bottle Opener 35 | 33 – 36 mm | - Juice Jug (Some brands) 1.89 L - Ketchup Bottle 1 L - Juice Carton 900 mL

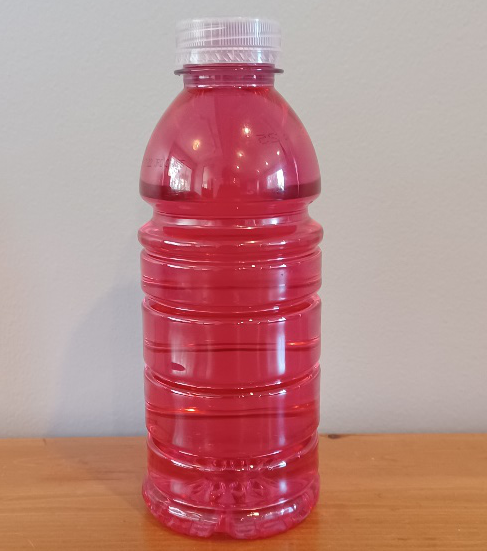
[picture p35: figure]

Bottle Opener 40 | 38 – 41 mm | - Sports Drink 591 mL - Sports Drink 950 mL - Juice Bottle 473 mL - Iced Tea Bottle 473 mL - Milk Bottle 473 mL - Milk Jug 2 L - Milk Jug 4 L - Kefir Bottle 1 L


Bottle Opener 45 | 43 – 46 mm | - Juice Jug 1.46 L - Juice Jug (Some Brands) 1.89 L - Juice Jug 945 mL


Bottle Opener 50 | 48 – 51 mm | - 3 L Juice Jug

## Cleaning

Clean with damp cloth, sterilize with disinfecting wipes or light spray. Do not submerge.

© 2022 by Neil Squire / Makers Making Change. This work is licensed under the CC BY SA 4.0 License: http://creativecommons.org/licenses/by-sa/4.0 Files available at https://makersmakingchange.com/project/bottle-opener/ Page 2 of 3

V1.0 | May 2022 Bottle Opener user Quick Guide

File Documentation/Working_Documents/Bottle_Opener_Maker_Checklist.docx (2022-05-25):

# Maker To Do List

- Talk to User about which bottles they would like to open, determine which sizes of Bottle Opener to print using the Printable Sizing Chart or examples list.
- Ask user about which colour they would prefer the device to be printed in.
- Print and test the device/devices.
- Print User Guide.

# Items to Give to User

- Printed, tested device/devices.
- User Guide.

© 2022 by Neil Squire / Makers Making Change This work is licensed under the CC BY SA 4.0 License: http://creativecommons.org/licenses/by-sa/4.0 Files available at https://makersmakingchange.com/project/bottle-opener/ Page 1 of 1

V1.0 | May 2022 Bottle Opener Maker Checklist

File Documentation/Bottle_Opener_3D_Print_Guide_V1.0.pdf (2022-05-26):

V1.0| May 2022

## Bottle Opener

## 3D PRINTING GUIDE

© 2022 by Neil Squire / Makers Making Change. This work is licensed under the CC BY SA 4.0 License: http://creativecommons.org/licenses/by-sa/4.0 Files available at https://makersmakingchange.com/project/bottle-opener/

### 3D Printing Summary

Metrics
Total Print Time (min) | 224 - 241
Total Number of Components | 1 - 5
Typical Total Mass (g) | 36 - 39
Typical Number of Print Setups | 1 - 5

### 3D Printing Settings

Print File Name | Qty | Total Print Time (hr:min) | Mass (g) | Infill (%) | Support | Layer Height/ Nozzle Diameter(mm) | Notes (orientation, special settings, etc.)
Bottle_Opener_30.stl | 1 | 3:47 | 37 | 50 | No Support | 0.2/0.4 | Adjust number of perimeters to 3-4.
Bottle_Opener_35.stl | 1 | 3:44 | 36 | 50 | No Support | 0.2/0.4 | Adjust number of perimeters to 3-4.
Bottle_Opener_40.stl | 1 | 3:46 | 36 | 50 | No Support | 0.2/0.4 | Adjust number of perimeters to 3-4.
Bottle_Opener_45.stl | 1 | 3:51 | 38 | 50 | No Support | 0.2/0.4 | Adjust number of perimeters to 3-4.
Bottle_Opener_50.stl | 1 | 4:01 | 39 | 50 | No Support | 0.2/0.4 | Adjust number of perimeters to 3-4.

### Post-Processing

- Remove any burrs or sharp edges that may occur if applicable.

### Customization Options

- There are parameters given in the CAD file (.f3d) to change the cap size and handle size if desired.
- Can be printed in any colour.

## 3D PRINTING GUIDE

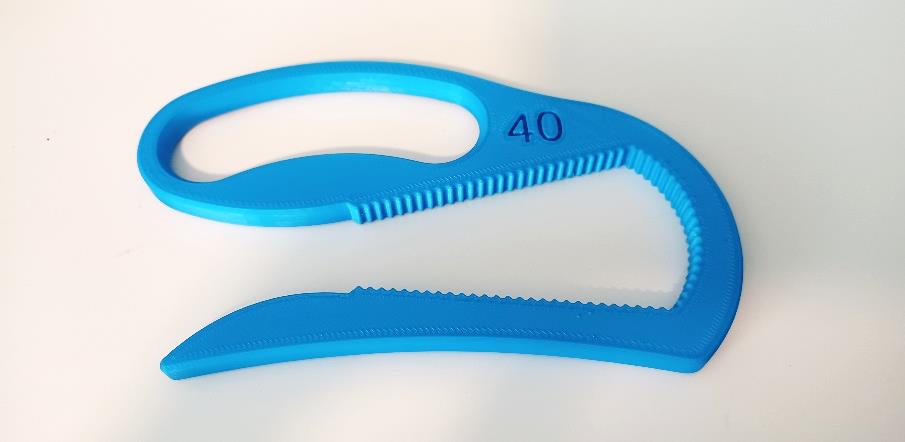
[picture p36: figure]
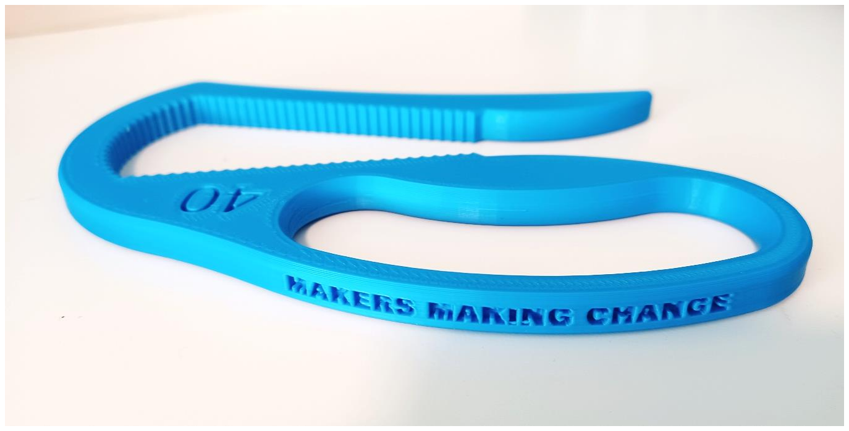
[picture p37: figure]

© 2022 by Neil Squire / Makers Making Change.

### Examples of Quality Prints:

Example of Bottle Opener 40

Example of Bottle Opener 40

## 3D PRINTING GUIDE

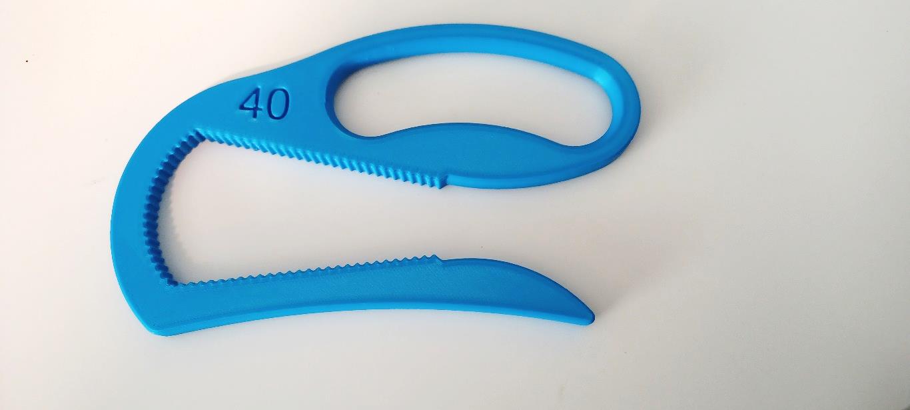
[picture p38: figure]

© 2022 by Neil Squire / Makers Making Change.

Example of Bottle Opener 40

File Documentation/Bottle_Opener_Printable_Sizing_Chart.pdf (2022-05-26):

To check if scale is correct,
the line below should be 100mm long.

50mm

45mm

40mm

35mm

30mm

# Printable Sizing Chart for Bottle Opener

To ensure a correct fit,

## bottle caps should fit

within the lines shown.

© 2022 by Neil Squire / Makers Making Change. This work is licensed under the CC BY SA 4.0 License: hp://creavecommons.org/licenses/by-sa/4.0
Files available at hps://makersmakingchange.com/project/bole-opener/ | Page 1 of 1

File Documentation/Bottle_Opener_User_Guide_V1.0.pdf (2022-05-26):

V1.0 | May 2022

## Bottle Opener

## USER QUICK GUIDE

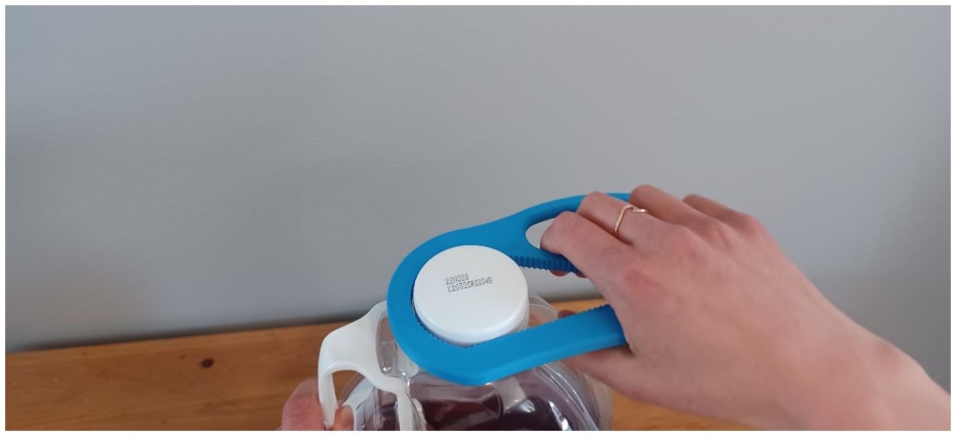
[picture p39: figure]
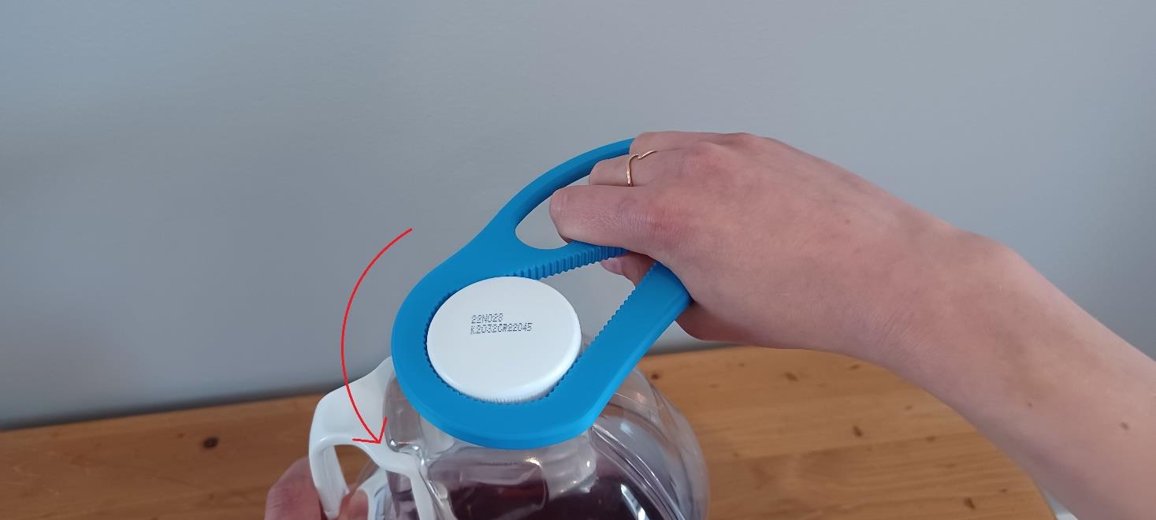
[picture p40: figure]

© 2022 by Neil Squire (https://neilsquire.ca/) / Makers Making Change. This work is licensed under the CC BY SA 4.0 License: http://creativecommons.org/licenses/by-sa/4.0 Files available at https://makersmakingchange.com/project/bottle-opener/

### Introduction

The Large Bottle Opener is a tool to help those with arthritis, limited finger dexterity or other related disabilities open the screw-on caps commonly seen on large juice jugs.

### Usage

Grip the bottle opener with fingers placed though the hole and palm on the bottom lever. Place the bottle opener over the lid of the bottle, squeeze the lever while twisting the cap off the bottle.

## USER QUICK GUIDE

© 2022 by Neil Squire (https://neilsquire.ca/) / Makers Making Change.

### Compatibility

Bottle Opener
Version

Compatible
Diameter of
Caps

Examples of compatible
Bottles and Containers
(May vary between brands)

Image Example of compatible Bottles

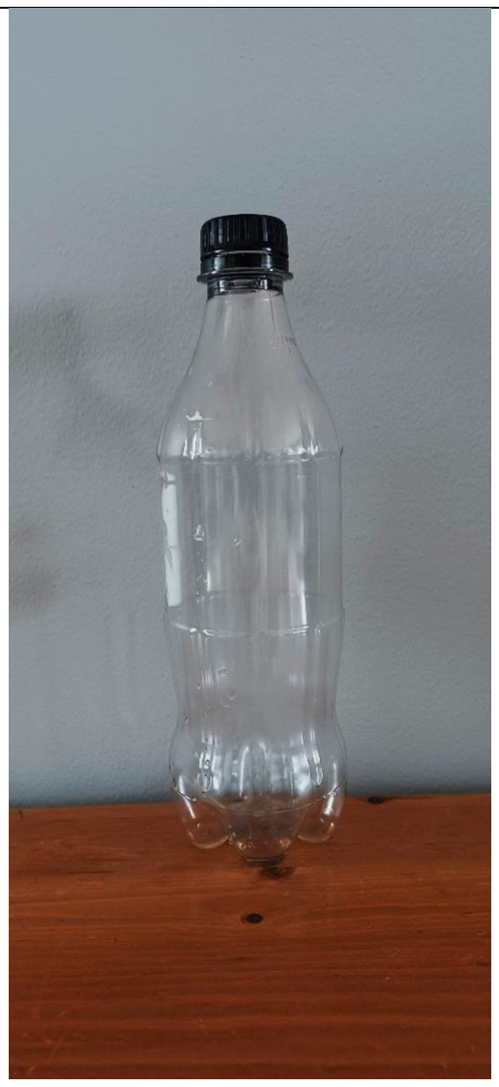
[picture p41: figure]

Bottle Opener
30 | 28 – 30 mm
- Pop bottles of all
sizes (355 mL to 2 L)
- Bottled Water of all
sizes (355 mL to 2 L)
- Milk Carton 2 L
- Juice Carton 2 L

## USER QUICK GUIDE

© 2022 by Neil Squire (https://neilsquire.ca/) / Makers Making Change.

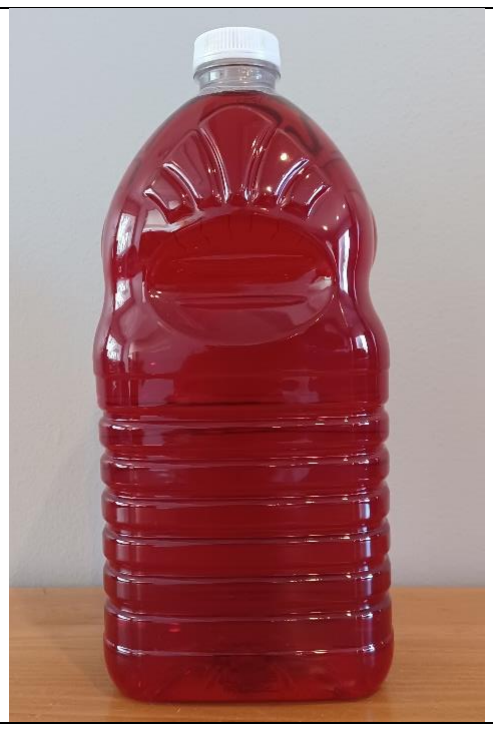
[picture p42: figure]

Bottle Opener 35 | 33 – 36 mm | • Juice Jug (Some brands) 1.89 L • Ketchup Bottle 1 L • Juice Carton 900 mL

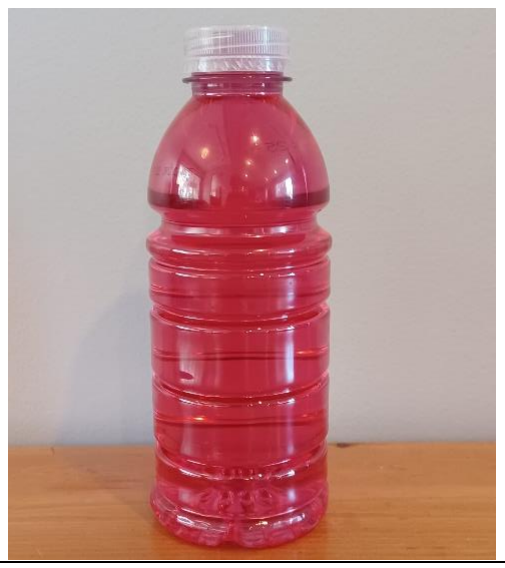
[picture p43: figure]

Bottle Opener 40 | 38 – 41 mm | • Sports Drink 591 mL • Sports Drink 950 mL • Juice Bottle 473 mL • Iced Tea Bottle 473 mL • Milk Bottle 473 mL • Milk Jug 2 L • Milk Jug 4 L • Kefir Bottle 1 L
Bottle Opener 45 | 43 – 46 mm | • Juice Jug 1.46 L • Juice Jug (Some Brands) 1.89 L • Juice Jug 945 mL

## USER QUICK GUIDE

© 2022 by Neil Squire (https://neilsquire.ca/) / Makers Making Change.

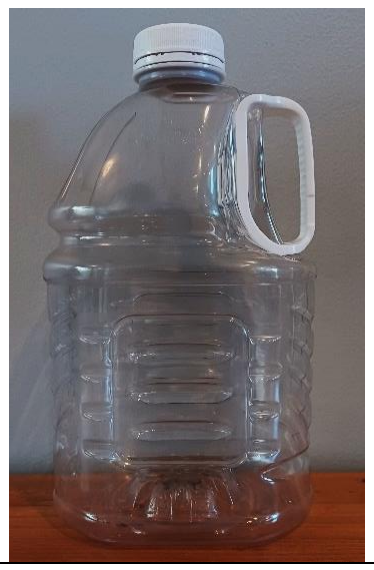
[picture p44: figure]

Bottle Opener
50 | 48 – 51 mm | • | 3 L Juice Jug

### Cleaning

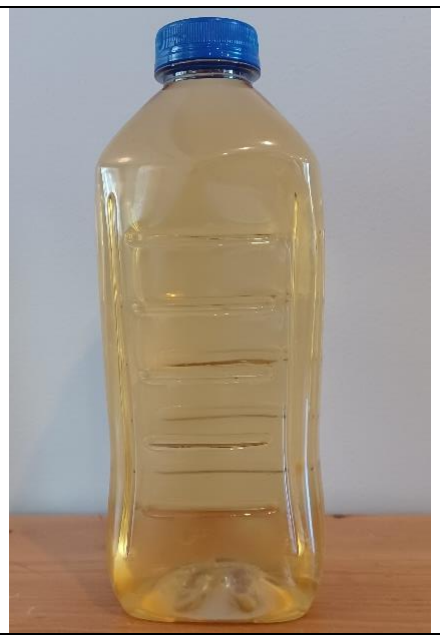
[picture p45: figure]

Clean with damp cloth, sterilize with disinfecting wipes or light spray. Do not submerge.

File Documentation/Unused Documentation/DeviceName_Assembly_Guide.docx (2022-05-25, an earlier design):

# Required Components

<Insert a photo with all components of the device laid out and labelled with number that correspond to the numbers in the cell to the right. Add appropriate Alt text> | BOM

# Required Tools

# Required Personal Protective Equipment (PPE)

# Assembly Instructions

## Step 1

<Description>

<Insert photo here. Make sure to add appropriate alt text>

## Step 2

<Description>

<Insert photo here. Make sure to add appropriate alt text >

## Step 3

<Description>

<Insert photo here. Make sure to add appropriate alt text >

<Add additional steps as necessary

© 2022 by <Author>. This work is licensed under the CC BY SA 4.0 License: http://creativecommons.org/licenses/by-sa/4.0 Files available at <Replace with MMC Library Link> Page 1 of 1

VX.X | <MONTH> <YEAR> <Device Name> Assembly Guide

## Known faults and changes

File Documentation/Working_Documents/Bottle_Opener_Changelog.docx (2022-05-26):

# Version 1.0 | Date 05/19/2022

- Created initial versions of Bottle Opener 50, Bottle Opener 45, Bottle Opener 40, and Bottle Opener 35.
  - Removed can tab opening feature from these designs.
  - CAD design and documentation by Neil Squire / Makers Making Change.
- Slightly modified Original Bottle Opener Design by adding an embossed size and removing the can tab opening feature. Renamed this design to Bottle Opener 30.

© 2022 by Neil Squire / Makers Making Change. This work is licensed under the CC BY SA 4.0 License: http://creativecommons.org/licenses/by-sa/4.0 Files available at https://makersmakingchange.com/project/bottle-opener/ Page 1 of 1

V1.0 | May 2022 Bottle Opener changelog

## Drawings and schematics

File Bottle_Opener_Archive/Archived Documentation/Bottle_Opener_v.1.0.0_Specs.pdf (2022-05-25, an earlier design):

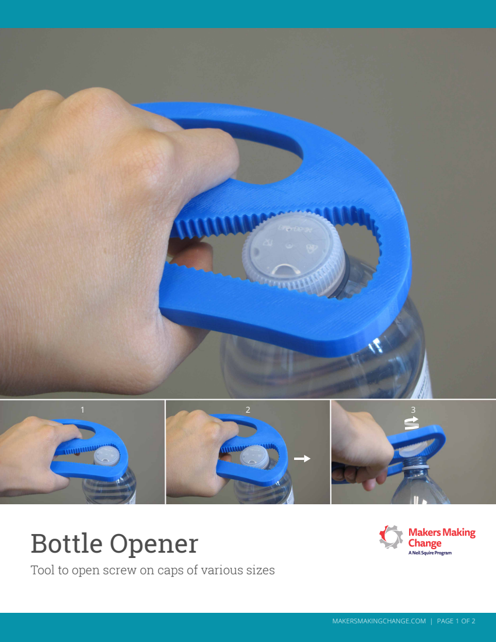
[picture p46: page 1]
Bottle Opener

Tool to open screw on caps of various sizes

MAKERSMAKINGCHANGE.COM | PAGE 1 OF 2

# Bottle Opener

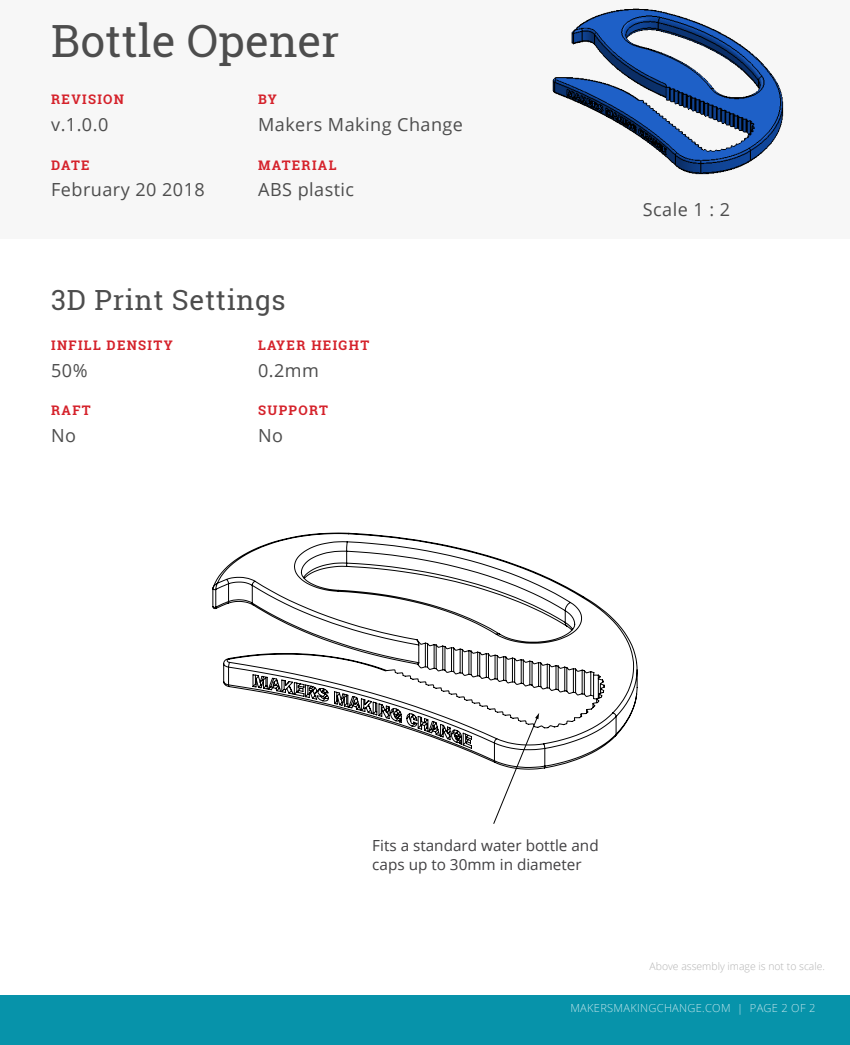
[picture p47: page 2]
DATE; MATERIAL; INFILL DENSITY; LAYER HEIGHT; RAFT; SUPPORT; 3D Print Settings; REVISION v.1.0.0; Scale 1 : 2; February 20 2018; ABS plastic

Makers Making Change

Fits a standard water bottle and
caps up to 30mm in diameter

Above assembly image is not to scale.

MAKERSMAKINGCHANGE.COM | PAGE 2 OF 2

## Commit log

2022-05-25 Edit to BOM and Summary
    [Bottle_Opener_BOM_V1.0.xlsx]
2022-05-25 Edit to BOM csv and Summary pdf
    [Bottle_Opener_BOM_V1.0.csv]
2022-05-25 Removed Comments from 3D Print Guide
2022-05-26 Fixed Footers and Sizing Chart
    Added missing project links and Author to changelog, 3d print guide and user guide. Added footer to Printable Sizing Chart. Added Inkscape svg for the Printable Sizing Chart to the working documents 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
2022-05-27 New Archive folder
    [Bottle_Opener_30.stl, Bottle_Opener_v.1.0.0.STL]
2022-05-27 Added Design File to Archive
    [Bottle_Opener_v.1.0.0 v1.f3d]
2025-04-28 Add step files
    [Bottle_Opener_30.step, Bottle_Opener_35.step, Bottle_Opener_40.step, Bottle_Opener_45.step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]
2025-04-28 Reorganize CAD Files
    [Bottle_Opener_30.f3d, Bottle_Opener_35.f3d, Bottle_Opener_40.f3d, Bottle_Opener_45.f3d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]
